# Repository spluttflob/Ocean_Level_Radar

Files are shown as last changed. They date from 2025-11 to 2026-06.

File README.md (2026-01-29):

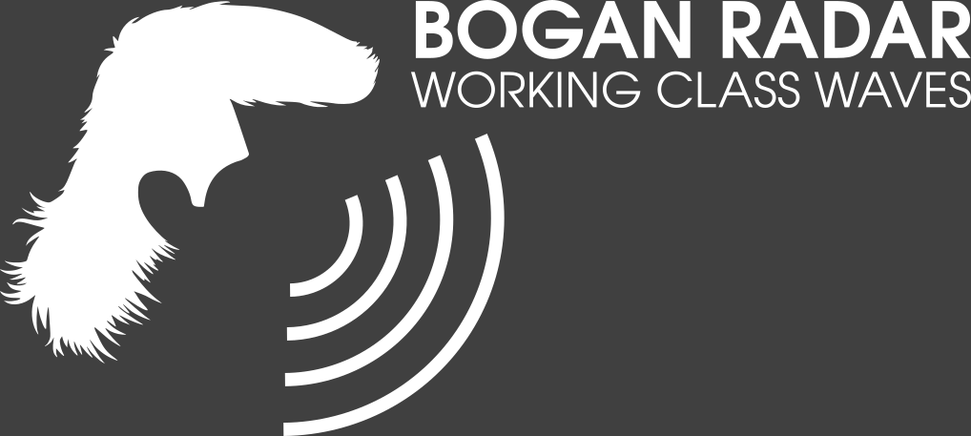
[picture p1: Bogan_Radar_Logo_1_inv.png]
Project logo


This project aims to create simple and inexpensive designs for measuring 
ocean level from piers, pilings, trees, or other relatively fixed
locations above the water.  THe measurements are to be taken quickly enough
that ocean waves and perhaps wind chop can be resolved. 
Ocean Science Hippies will use these measurements to better understand the 
effects of tides, waves, tsunamis, sea level rise, and other ocean phenomena 
on the coastal environment. 

## Hardware

The custom circuit board design currently used is in `hardware`. 

Mechanical part designs, including radar antennas and lenses, are currently 
being developed and will be added to this repository if and when we figure out
what on Earth we're doing. 

### Power

The current (2026 January) hardware versions may be powered by connecting the
ESP32 to a laptop through a USB cable, **or** by supplying the system with 
5 volts DC through the water resistant connector on the box. 

If a laptop cannot supply enough current through its USB port, the ESP32 may
reboot due to low supply voltage (it says `brownout detected`.)  Usually, 
rebooting a couple of times causes it to come to life; if that doesn't work, 
try another laptop and/or a powered USB hub. 

<span color="red">Only one source of power should be used at a time; **do not** 
connect the ESP32 Feather to a PC while DC power is being supplied through the 
waterproof connector.</span>

## Firmware

The software currently being developed uses a MicroPython program running on an
ESP32 as the overall controller, data logging, and network interface computer.
There is an STM32 microcontroller in the XM125 radar module which runs it own
software which is written in C. 

### ESP32 Firmware

There are two versions of the software which have been developed. The first
version is written in C++, and the second (and currently being worked on) 
version is in MicroPython.

#### C++

The C++ ESP32 firmware is in the `WaterSense_Radar_JJH` directory. 
After cloning this repository, open the `WaterSense_Radar_JJH` directory in a
VSCode/PlatformIO workspace and you should be able to compile and run the
ESP32 firmware. It requires custom firmware to be running on the STM32 in
the XM125 module.

#### MicroPython

For rapid development and testing, MicroPython firmware is provided in the
`MicroPython` folder.  MicroPython for the ESP32 can be downloaded from:  
<https://micropython.org/download/ESP32_GENERIC/>  
The latest release of the `ESP32_GENERIC` software is recommended for our
Feather circuit boards. 

With MicroPython installed on the ESP32, all the Python source files should 
be copied to the root directory of the ESP32's MicroPython filesystem, and 
`radar.cfg` should be copied to the root directory of the ESP32 file
system. Configuration of the system for use at specific sites may require 
editing of `main.py` and `task_mqtt.py`. The main Python file is edited to 
disable unneeded tasks; for example, the MQTT task should be turned off 
(just comment out the `asyncio.create_task()` line) at sites where WiFi 
access and AC power are not available. The radar's range, frequency of data 
collection, and similar configurations are set in `radar.cfg`. 

##### MicroPython File List

The following files need to be uploaded to the root directory of the ESP32's
MicroPython filesystem:

* `as_GPS.py` -- The asyncio GPS file from 
  <https://github.com/peterhinch/micropython-async/tree/master>
  or use the older, unmaintained copy here.
  
* `as_xm125_distance.py` -- From this repository.

* `main.py` -- From this repository.

* `mqtt_as.py` -- The asyncio MQTT client from
  <https://github.com/peterhinch/micropython-mqtt>
  or use the older, unmaintained copy here

* `pcf8523.py` -- Driver for the PCF8523 real-time clock on the Adalogger.
  Modified from others' work; use the copy here.
  
* `queue.py` -- From the standard MicroPython queues at 
  <https://github.com/peterhinch/micropython-async/tree/master>
  again, with an old local copy here for convenience.

* `task_gps.py` -- GPS task file from this repository.

* `task_mqtt.py` -- MQTT task (used if you have AC and WiFi) from this repository.

* `task_sd_card.py` -- SD card task from this repository.

* `radar.cfg` -- The configuration file for each site, put on the SD card.

#### Configuration with `radar.cfg`

The configuration file is a regular text file saved on the data logging SD card.
A typical configuration file might look as follows (for 2025-Dec version of the 
software; configurations are expected to change as the software is improved):
```txt
# Configuration file for Bogan Radar

Site Name:           My_Bench   # Name of site; should be one word (no spaces)
Beginning Distance:  2.0        # Beginning distance (m)
Ending Distance:     8.0        # Ending distance (m)
Sensitivity:         500        # Peak threshold sensitivity
Time Per Point:      5.0        # Time between data points (seconds)
Awake Time:          0.0        # Time taking data, sec., or 0.0 for always awake
Cycle Time:          0.0        # Total on-off cycle time, or 0.0 for always awake
```

_With changes to the value of `SD_DIR` in `task_sd_card.py`, the configuration
file could be saved in the ESP32's built-in flash; this would make reconfiguration 
a little harder but protect the configuration from SD card corruption due to power 
loss, somebody hot swapping the card (bad idea), etc._

If data is sent through MQTT, the MQTT topic is made by appending the site name
from the configuration file to `bogan_radar/`. 

### STM32 on XM125 Firmware

The STM32 microcontroller on the XM125 radar can be given a custom program to
optimize the radar module for our use. We have two setups available:

* When using the MicroPython firmware on the ESP32, the XM125's STM32 must be
  flashed with Acconeer's standard distance measurement application.
  The Acconeer software is available from:  
  <https://developer.acconeer.com/home/a121-docs-software/xm125-xe125/>  
  (You have to enroll with a developer account, but at least it's free to do 
  so.)

* When using the C++ firmware from directory `WaterSense_Radar_JJH` for the 
  ESP32, the source code for the STM32 microcontroller in the XM125 radar 
  module from subdirectory `xm125` must be compiled and flashed to the XM125.
  Compiling the XM125 STM32 code is a bit of a hassle, so we can use a binary 
  copy of the last working code.
  
* It's convenient to use an ST-Link2 programmer to flash the STM32 code to the 
  radar module. There is an ST-Link2 compatible 6-pin programming header near
  the screw terminal on the main circuit board, and there are two pushbuttons
  on the board to reset the STM32 and to put the STM32 in bootloader mode if 
  needed. 

## PC Software

### The _Acconeer Exploration Tool_

This handy application consists of a firmware package and a PC application.
Although it's designed to be run on an official Acconeer development board, the
Exploration Tool can also be run on our boards.

Instructions for setting up the STM32 firmware and Python PC software are at
<https://github.com/acconeer/acconeer-python-exploration>.  Follow Acconeer's 
instructions **with the following exceptions:**

* We usually use leftover ST-Link2 programmers (from old STM32 Nucleo&trade; boards) 
  instead of fussing with DFU programming.  The 6-pin ST-Link2 header next to 
  the power and battery connectors is connected directly to the 6-pin `SWD` (CN4) 
  connector on the ST-Link2, matching the ends marked with dots or triangles. 
  The STM32 Cube Programmer&trade; is a convenient way to flash the binary file
  for the firmware to the STM32. 

* To use our boards with the Exploration Tool, first remove the ESP32 Feather 
  board, any FeatherWing accsesory boards, and the GPS module from the main radar 
  circuit board. Leaving the GPS antenna in place, if present, is OK. 
  Then attach a connector (header pins or sockets) to the three-pin header pad
  marked `STM32 UART0` in the area where the GPS board sits.  Connect a USB to
  RS-232 serial adapter to STM32 UART0 pins, remembering the annoying RS-232 
  standard where RXD of one device must connect to TXD of the other. 
  If you're a civil, environmental, or mechanical engineer: Don't forget the 
  ground wire!  `:)`
  The Exploration Tool should now be able to connect to the XM125 as if the
  XM125 were on the official evaluation board. 

<!-- 
* Use ST-Link to load firmware
* Connect USB-Serial to ST's UART
* Set up Exploration Tool on PC
--> 

### Plotting MicroPython Data

If MicroPython is used, data will be saved in a Semicolon And Comma Separated
Variable (`.sacsv`) format. Some simple programs to plot data in this form are
being developed and can be found in the `CPython` directory. 

An older plotting program (look for lower numbers) uses data in a format 
without the date on each reading; this has caused some inconvenience, so newer
data is saved will a full datetime on every reading, and newer CPython scripts
with higher numbers in the file names use the newer format. 

### Plotting C++ Firmware Data

Some more fully Python developed programs to analyze data from the C++ firmware 
are in the `ESP32_to_Python_GUI` directory. 

It is our intention to merge the capabilities of the CPython programs from
the `CPython` and `ESP32_to_Python_GUI` directories to create especially 
convenient and flexible data analysis and plotting applications. 

## References

* A Masters thesis utilizing ultrasonic rather than radar sensors which gives
  some perspective to the project:  
  <https://digitalcommons.calpoly.edu/theses/2745/>

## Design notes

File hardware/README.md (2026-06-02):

# Bogan Radar Hardware Notes

**Version 1.4 (Still in alpha)**

This newer board is simpler and easier to assemble than V1.3.  All the SMD parts
are on one side of the board, so the SMDs can be soldered on first; a hot plate
works pretty well for this.  After the SMDs are in place, the through-hole parts 
can be attached to the other side.  The assembly of the board to the radar
antenna and installation in an enclosure are the same for both boards. 

**Version 1.3 (Obsolete; do not use)**

_**NOTE:** The 1.3 board version has not performed well enough in testing and is
considered obsolete. Newer boards are being prepared. The process of installing
the newer boards will be the same as that of installing older boards._

The current design uses the following bits:

* An Acconeer&trade; XM125 radar mounted to the bottom of a circuit board, with
  headers for many of the XM125 pins broken out to through holes on the board

* An Adalogger&trade; Featherwing for its SD card and battery backed up 
  real-time clock, mounted in a socket atop the board using stacking headers

* An ESP32 Feather board (EZSBC made boards preferred) mounted atop the 
  Adalogger
  
* A generic GPS receiver atop the circuit board

* A LiPo battery charging circuit built into the Feather board

The radar system is enclosed in a generic waterproof junction box. 
The board is mounted atop a horn-type millimeter-wave antenna that is attached
to the box with a waterproof seal.  The system is watertight so that it has a
chance to survive when deployed just above the ocean. 

_Note from testing: The enclosure shown has been tested in and survived 
several rainstorms, though a small amount of water was found in the bottom of
the box after about 6 weeks and several storms._

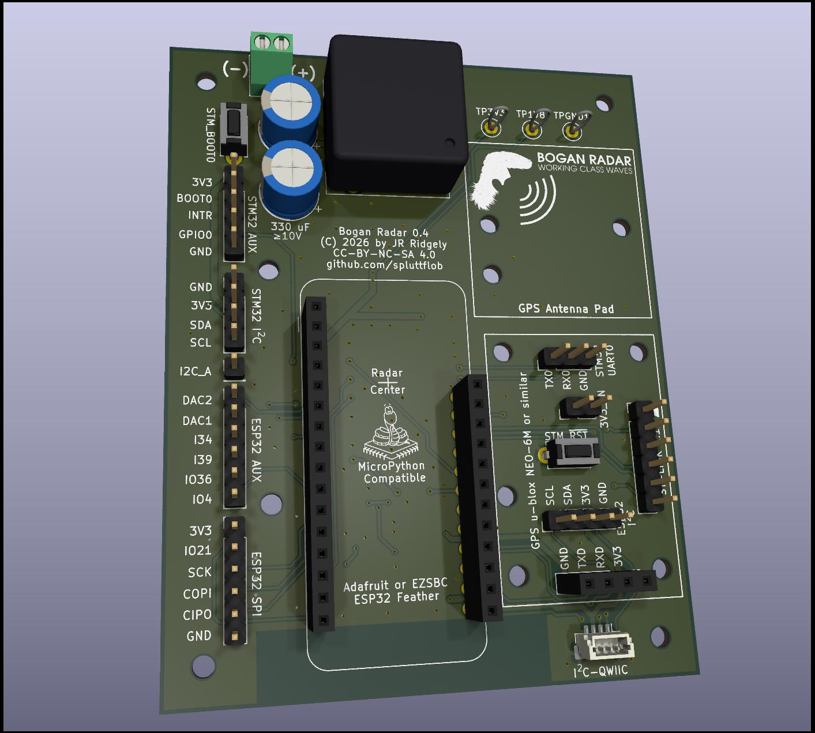
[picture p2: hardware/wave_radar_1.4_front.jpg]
Rendering of Board V1.4 Top Side


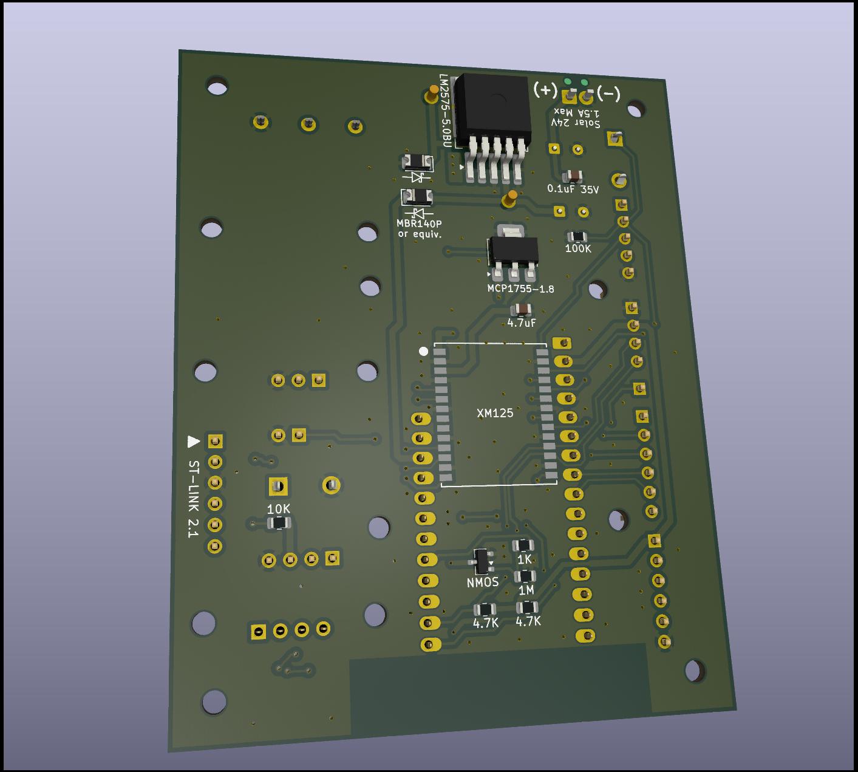
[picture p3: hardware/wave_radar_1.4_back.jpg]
Rendering of Board V1.4 Bottom Side


## Board V1.3 Hacks (legacy; use newer boards)

The design of the system has changed since a batch of the Version 1.3 boards
was manufactured, so there have been some hacks made involving jumper wires.
Please see [HACKS_1.3](HACKS_1.3.md) for details.

## RADAR Antenna

The horn antenna is a simple cylindrical design, manufactured mostly using a
lathe:

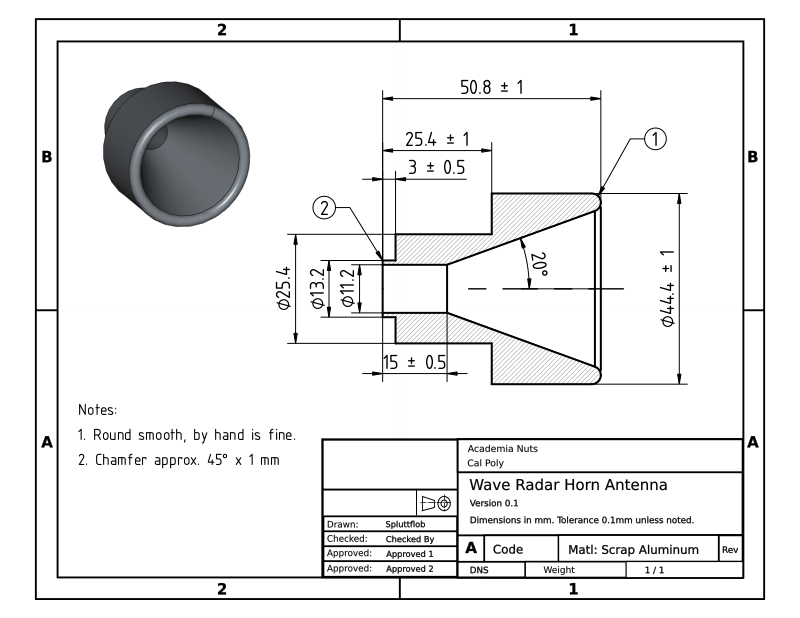
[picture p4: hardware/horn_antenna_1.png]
Drawing of Antenna


There are other antennas available such as plastic lenses. These may work well
also, and antenna testing and comparison are ongoing.

## Mounting in Enclosure

The branding of a typical enclosure is shown below.  This is not an endorsement
of this particular enclosure above others; it's just something we've tried:

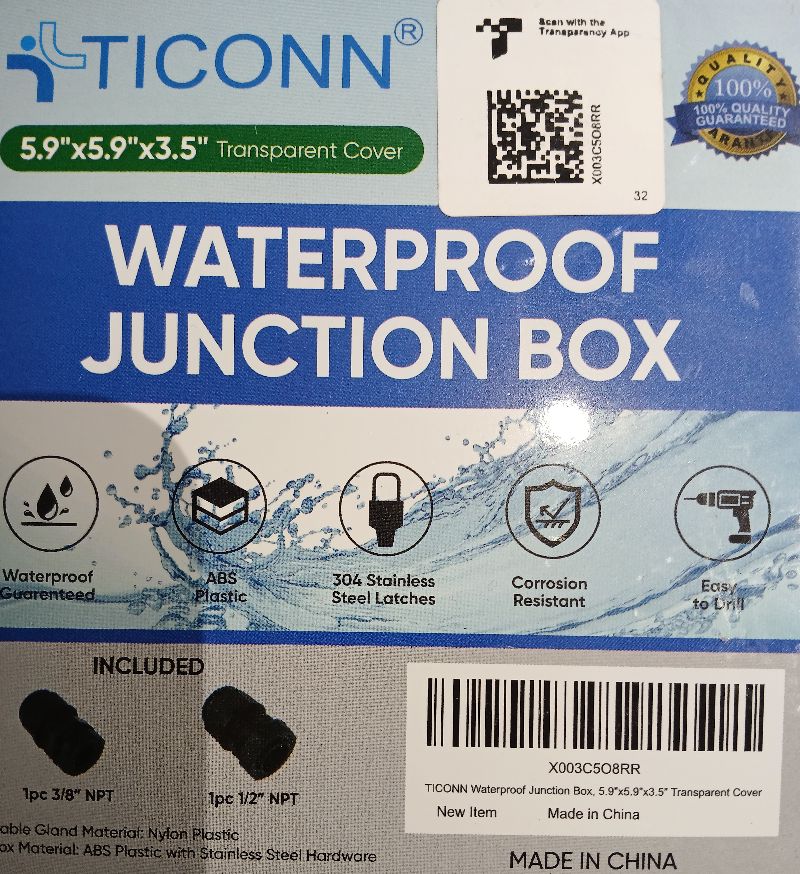
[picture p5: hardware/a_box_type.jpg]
Radar Box Brand


The antenna is mounted in the bottom of the box. A 1 inch hole is cut for the
antenna and the antenna is pushed in from the outside. We have had good results
using a step drill to make the hole.  Sealant is applied to
the flat mounting face of the antenna to prevent water ingress, and a couple of 
\#6-32 screws are tapped into the mounting face of the antenna to secure it to 
the box:

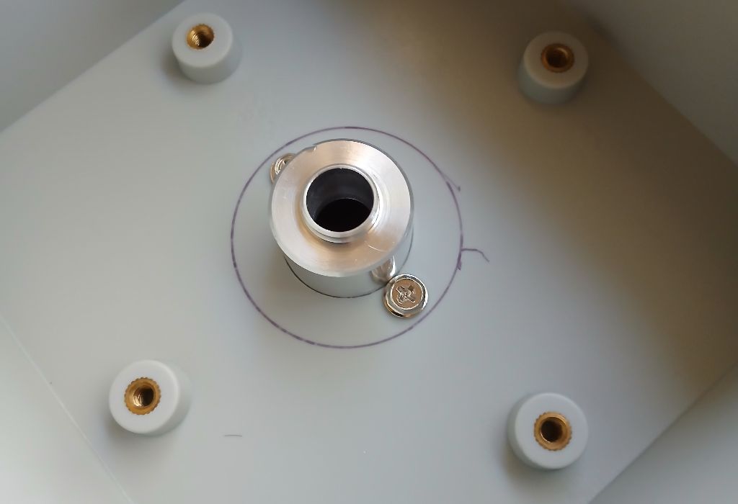
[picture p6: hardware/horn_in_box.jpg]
Box with Antenna Mounted


A 3D printed board mounting piece is attached to the upper side of the antenna 
to mount the circuit board. The end of the antenna must be flush with the slot
in the face of the board mount, as shown below using a ruler to verify that the
board mount is at the correct height. It's a little hard to see in the photo,
but the edge of the ruler is down in the slot, _not_ up on the faces of the
board mount that contact the board. This is critical because the XM125 sensor
will be in that slot when the board is mounted:

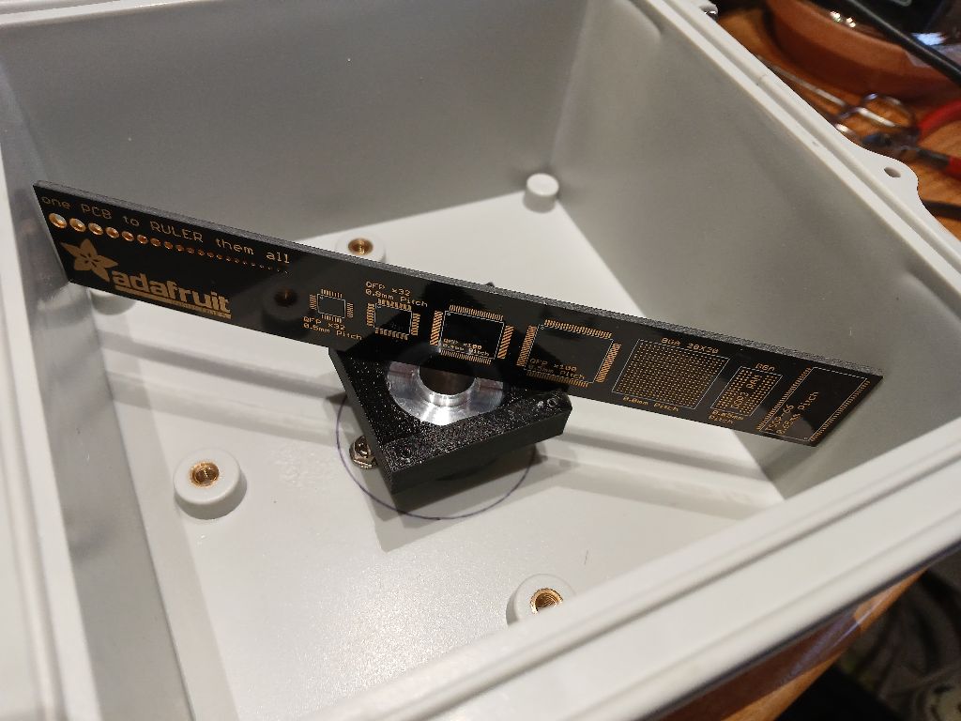
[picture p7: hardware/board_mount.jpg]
Attaching board mount at correct height


The board attaches to its mount with four annoyingly tiny screws. Ensure that
nobody sneezes to prevent losing the screws.  After the board is mounted, the
Featherwing, ESP32, and GPS can be inserted in their sockets and the electrical
power connection (see below) hooked up. 

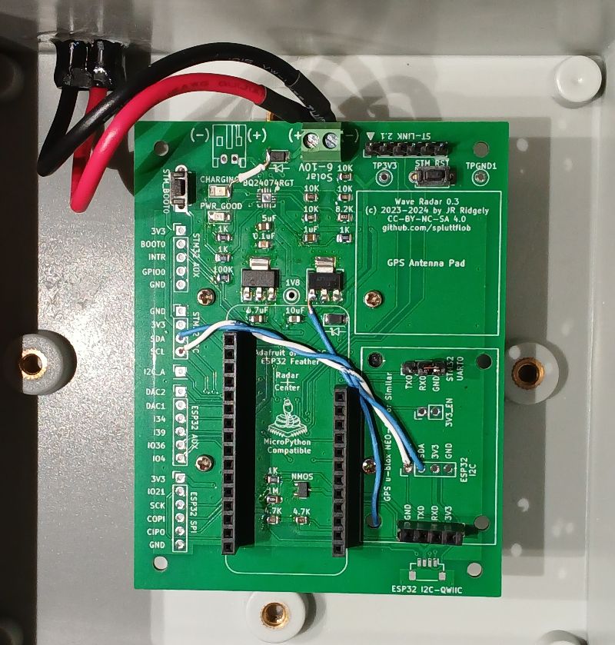
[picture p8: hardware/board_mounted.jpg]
Board attached to the board mount


The ESP32 Feather and Adalogger boards are stacked onto the Feather connectors
on the board in the usual way. Depending on the type of GPS module used, one
may need to mount the GPS antenna separately from the GPS module board.  If so,
the antenna can be mounted to the area marked `GPS Antenna Pad` on the board
with some double-sided foam tape. 
It is recommended to mount the GPS antenna so that the board mounting screw is
easily accessible with a screwdriver, as the need to remove the board for
updates or repairs is all but guaranteed in a research project. 

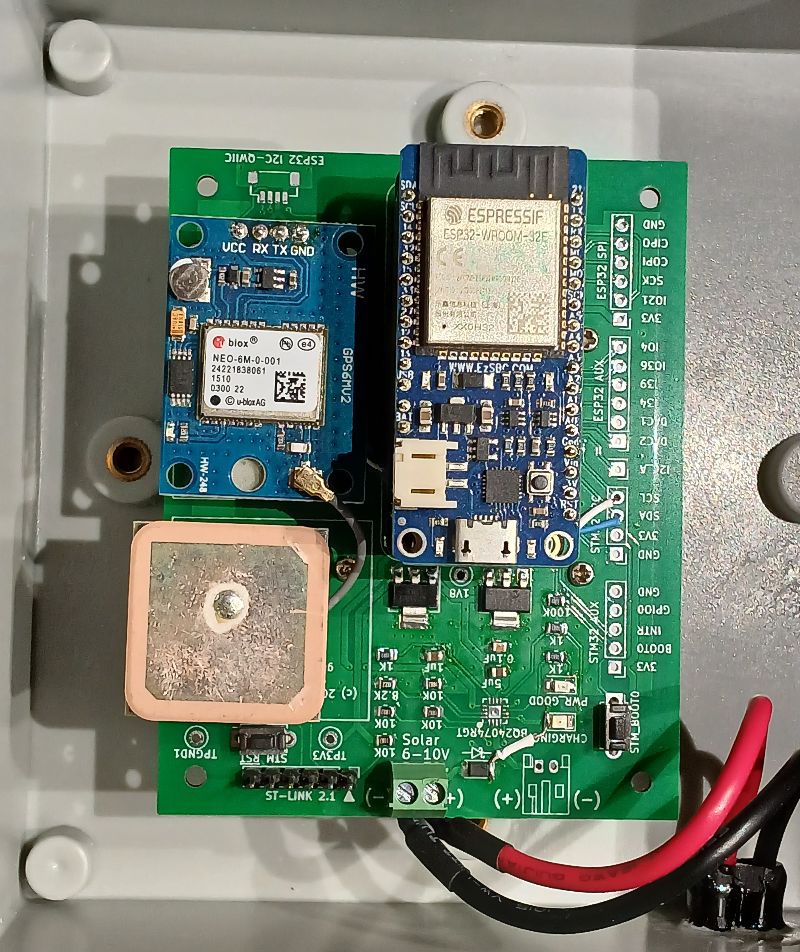
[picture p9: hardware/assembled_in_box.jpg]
Board with all parts attached


## Electrical Power Connection

For most uses, electricity must be supplied to the radar system from outside, 
either a solar panel or 5 volt wall plug adapter. _**Note:** The adapter should
be rated to produce 5.0 to 5.2 volts at around 1 amp. EZSBC boards are
designed to be supplied from 5 volt USB supplies and rated to handle up to 5.5
volts._  The power connection must be watertight.  In an experimental setup, we
have used an inexpensive waterproof automotive style connector glued into a hole
in the side of the box. 

## Radar Antenna Cover

This is an area of ongoing research. The radar may have an optimally tight beam
if a plastic phase corrector is attached across the bottom (wide) opening of
the horn antenna, but for initial testing we're trying polypropylene and
polyethylene disks made from various containers. The cover's ideal width which 
minimizes reflections of the 60GHz signal depends on the material used. 
The Interwebs seem to say that a 1.5mm (about 1/16") sheet of polypropylene 
would make a good cover. Disks of UHMW polyethylene (we think) cut from a
Tupperware&trade; bowl lid saved from a dumpster seem to work pretty well too.
More will be posted when we have conducted more experiments. 

Remember that the cover must be attached to the end of the horn with a 
watertight connection to protect the sensor from rain, waves, spray, and
errant organisms. A version of the aluminum horn antenna which has a threaded
end, combined with a threaded PVC ring that holds a cover firmly against the
end of the antenna, seems to work well.  We may use a bit of caulk or pipe
dope to ensure a good seal.

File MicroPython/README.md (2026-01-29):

# Bogan Radar MicroPython Setup

The MicroPython program used in the current (2026 January) version of Bogan 
Radar has the following features:

* Data taken from XM125 radar at intervals of 5 seconds, with moderate timing
  accuracy. A system timer is used to minimize clock drift; each reading may be
  some milliseconds late, but subsequent readings are then made sooner to keep
  the overall timing accuracy as good as possible using cotasks.

* Data is saved to an SD card. Every few minutes, the file is opened, a batch
  of data is written, and the file is closed immediately thereafter. Having the
  file open for only a short time reduces the likelihood of data corruption on
  the card due to power losses or program crashes. 

* The ESP32's Real Time Clock (RTC) is assisted by a PCF8523 RTC on the SD card
  (data logger) circuit board. With a backup battery, the PCF8523 keeps time
  with the main power off; the ESP32 RTC loses track of time when power is lost.
  A GPS receiver module is used to set both RTC clocks, as the RTC clocks are
  not highly accurate and may lose a few seconds each day. 

* Data may be transmitted to an MQTT broker for capture and storage on a 
  computer at a remote site. A Raspberry Pi in the developer's closet is used
  for testing, but any old computer which can run an MQTT client can do the job;
  a low-power device is recommended to avoid wasting lots of energy keeping a
  PC running 24/7. 

* A tiny web server allows anyone with network access to the ESP32 through LAN 
  or its access point to download data files from the SD card, _if_ the system
  has been set up with WiFi access or it is set up as an access point.  Since
  the WiFi module in the ESP32 takes a lot of power, this capability is likely
  to be used only where an AC mains connection is available to the radar unit.

* To keep the system going in case of unexpected crashes, a watchdog timer is
  used.  The hardware watchdog timer in the ESP32 is used as well as a set of
  asyncio events that require the radar, SD card, and MQTT tasks to be working
  to prevent system resets. 

## Saving RAM

The ESP32 WROOM module used has limited RAM, and MicroPython is fairly resource
heavy. The program as currently used will run out of RAM and crash if all the
files are regular Python source files. 

Therefore, we upload many of the utility programs as byte-compiled `*.mpy` 
files; this reduces RAM usage somewhat and enables the program to run reliably.
The program `mpy-cross`, which is part of the MicroPython source code
distribution, is used to byte-compile MicroPython source code into `.mpy` 
files. See:  
<https://pypi.org/project/mpy-cross/>

<https://github.com/micropython/micropython/tree/master/mpy-cross>

For a technical discussion of `.mpy` files (probably not needed), see:  
<https://docs.micropython.org/en/latest/reference/mpyfiles.html>

The main file and task files are usually kept as regular Python source files
because we're editing them often to change program behavior, fix bugs, _etc._

## What Files?

An image of the file listing from a working Bogan Radar ESP32 file system is
shown below.

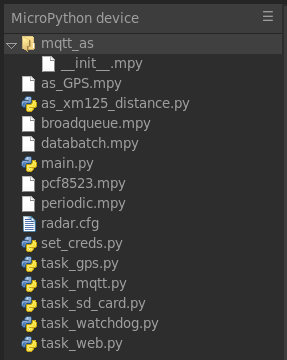
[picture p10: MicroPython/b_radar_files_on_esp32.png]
Device File List


It's a little weird that the asyncio MQTT server is in a file `__init__.py` in
the `mqtt_as` folder on the ESP32 filesystem. It's that way for reasons of
convenience due to how the `mqtt_as` system is distributed; it's easier to just
follow the distribution (with a small subset of its files to save space) than 
reorganize the package. 

## Configuration

We find the Thonny IDE at <http://thonny.org> convenient for editing files on 
the ESP32. 

* To change radar operating parameters such as site name, minimum and maximum 
distance to the water, and time between data points, edit `radar.cfg` on the
ESP32 filesystem. 

* To change the MQTT server and MQTT topic, edit `task_mqtt.py` where all the
  necessary information is in constants near the beginning of the file. 
  We've been using `test.mosquitto.org` for testing. 

* To set the LAN SSID and password:

  * Run the script `set_creds.py` on the ESP32. This script will define a
    function `setlan()` which allows the SSID and password to be stored in the
    ESP32's nonvolatile memory -- but it will _not_ run the function. 
    
  * You should then call the function, giving it the SSID and password of the
    access point you plan to use, for example:  
    `setlan("my_lan_name", "lamepassword")

If you're not using MQTT or the file server, turn off the tasks and make sure
the watchdog task won't be expecting the MQTT task to keep reporting to it:

In `main.py`:
```.py
    batch = databatch.DataBatch(POINTS_PER_DATA_BATCH,
                                maxsize=MAX_DATA_QUEUE_SIZE, drop_old=True)
    consumer_A = batch.register()
   # consumer_B = batch.register()

    tasks = []
    tasks.append(asyncio.create_task(task_sd_card.task_SD_Card(consumer_A)))
   # tasks.append(asyncio.create_task(task_mqtt.mqtt_task(consumer_B)))
    tasks.append(asyncio.create_task(task_gps.gps_task(i2c, batch)))
    tasks.append(asyncio.create_task(task_radar(batch)))
    tasks.append(asyncio.create_task(task_watchdog.task_watchdog()))
   # asyncio.create_task(task_web.file_server_task())
```

In `task_watchdog.py`:
```.py
    await asyncio.gather( # mqtt_event.wait(),
                        sd_card_event.wait(),
                        radar_event.wait())
```

At this time, the file server task relies on the MQTT task to keep up a network
connection, so those two tasks must be activated or deactivated together. 
A future project should be to make an independent task which keeps the network
going for only the file server task. In addition, the web server could be 
kept off to save energy unless it is activated by some mechanism such as a
physical switch.

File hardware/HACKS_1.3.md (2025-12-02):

# Bogan Radar Board V1.3 Hacks

## I&sup2;C Connections

The method of communication between the ESP32 system control and networking 
microcontroller and the STM32 microcontroller on the XM125 radar board has been
changed from RS-232 to I&sup2;C.  Therefore, jumper wires must be connected 
between the ESP32's I&sup2;C terminals and those of the STM32. The twisted blue 
and white wires boing mostly left to right in the photo below connect the 
I&sup2;C signals. 

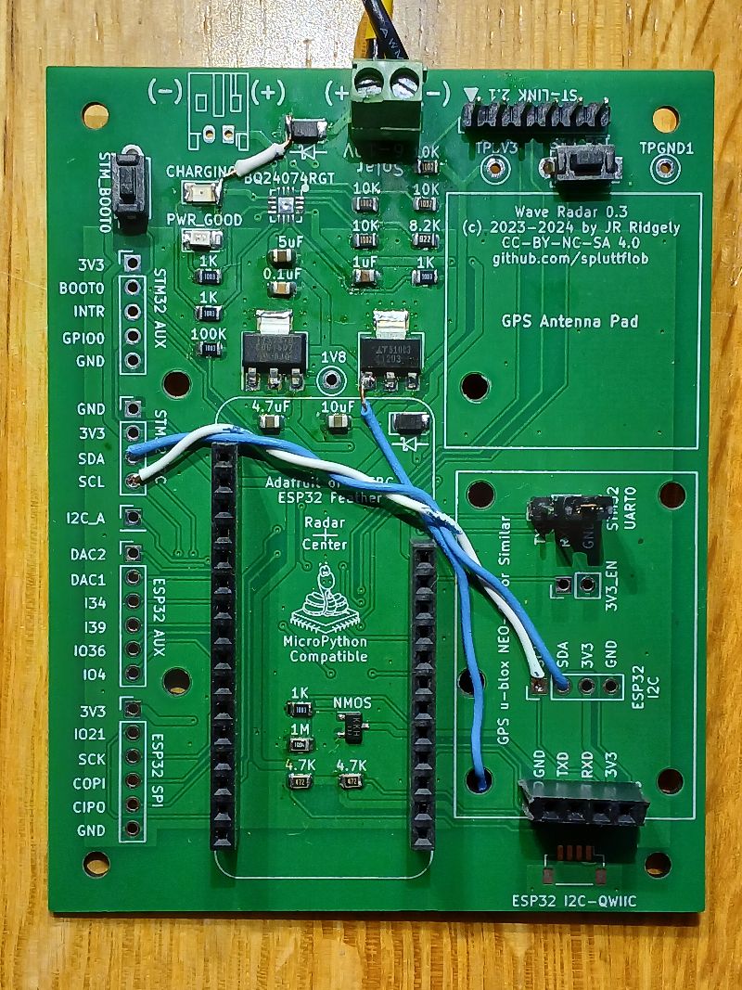
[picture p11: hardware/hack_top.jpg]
Main board with jumper wires all over


If the main board has been assembled correctly, the two 4.7K I&sup2;C pullup
resistors are already present. 

## AC _vs._ Solar and Battery Power

When deployed near a usable source of AC power, the radar system may be supplied
from a 5V DC adapter connected through the solar panel input. This connection is
made using the screw terminal at the top of the image above. _**Note:** 
Significantly higher voltages such as 12V should **not** be used, as the
regulators on the ESP32 Feather board are designed for 5V USB input and not
safe with higher voltages._ 

When using AC power, we can leave the BQ24074RGT charge controller off the 
board, bypassing it with a short wire such as the short white wire seen from
the right side of the CHARGING LED to the left side of the Schottky diode near
the screw terminals.  This supplies power to the 1.8V and 3.3V regulators on
the main board. 

In addition, power must be supplied directly from the input to the regulators
to the ESP32 Feather's USB power input.  The blue wire attached to the input
pin of the 3.3V regulator and extending downwards through an unused mounting
hole on the board does this.  This wire is connected to the ESP32 USB pin on 
the bottom of the board as seen in the photo below. 

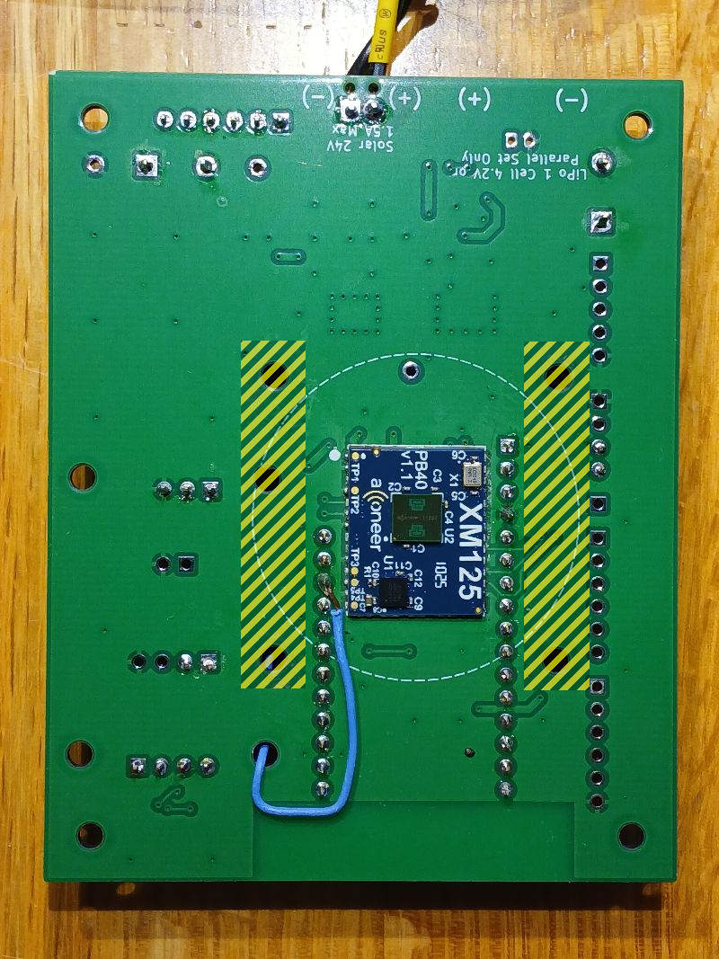
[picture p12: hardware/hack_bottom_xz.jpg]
Back of main board with a jumper


_**Note:** The jumper wire should not pass through the holes which are closer
to the XM125 because doing so will interfere with the mounting fixture and 
screws that are used to attach the board to the antenna. The board must be
mounted correctly to the antenna for a strong signal to be received.  Also
note that the wire is on the right side of the Feather mounting pins because
the board mounting fixture must be up against the board on the left side; the
approximate area where the board contacts the mounting fixture is crosshatched
in the image above._

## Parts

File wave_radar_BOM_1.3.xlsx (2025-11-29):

BOM For Wave Radar Version 1 -- Last Updated Nov. 2025
Parts on PCB (Board version 0.2) |  |  |  |  | Some quantities are greater than fit on boards to provide spares and/or take advantage of quantity pricing.
 | Id | Designator | Footprint | Brd.Qty. | Designation | Qty. For 5 Units | Cost / 5 Boards | Supplier and ref
 | 4 | J5 | JST_SH_BM04B-SRSS-TB_1x04-1MP_P1.00mm_Vertical | 1 | I2C-QWIIC | 1 pack | $3.95 | https://www.adafruit.com/product/4208 | Not needed for current system
 | 5 | R4 | R_0805_2012Metric | 1 | 8.2K | 10 | $0.07 | https://www.mouser.com/ProductDetail/YAGEO/RC0805JR-078K2L?qs=KyGMWp10UkvZ9xktQXin5g%3D%3D
 | 6 | J9 | JST_PH_S2B-PH-K_1x02_P2.00mm_Horizontal | 1 | LiPo | 5 | $0.90 | https://www.digikey.com/en/products/detail/jst-sales-america-inc/S2B-PH-K-S/926626
 |  |  | Mouser listing for S2B-PH-K connector above (I think!) | 1 |  | 10 | $2.27 | https://www.mouser.com/ProductDetail/JST-Commercial/S2B-PH-K-S-GWPP
 |  |  | Pushbutton switches...out of stock 2025-Nov-10 |  |  | 10 |  | https://www.mouser.com/ProductDetail/Apem/MJTP1243?qs=Uv2m1HzDAyqvmQR%252Bfj6VKQ%3D%3D
 | 10 | J10 | PinSocket_1x04_P2.54mm_Vertical | 1 | GPS | 5 | $3.97 | https://www.mouser.com/ProductDetail/Harwin/M20-7820442?qs=vF78I%252BjhbY9ZgDLCXkGx4w%3D%3D
 | 11 | R10,R9,R3,R8 | R_0805_2012Metric | 4 | 1K | 25 | $1.07 | https://www.mouser.com/ProductDetail/Bourns/CRT0805-FZ-1001ELF?qs=zVPOhnWuw8XKnszaWxnxVA%3D%3D
 | 12 | D3 | LED_1206_3216Metric (yellow) | 1 | CHARGING | 10 | $2.43 | https://www.mouser.com/ProductDetail/Kingbright/APD3224SYCK-F01?qs=VdjlWU%2FzoOF7uyPL3qtctA%3D%3D
 | 30 | D2 | LED_1206_3216Metric (green or blue) | 1 | PWR_GOOD | 10 | $2.49 | https://www.mouser.com/ProductDetail/Kingbright/APD3224SGC-F01?qs=VdjlWU%2FzoOFlLUgo8Vdl7g%3D%3D
 | 13 | Q1 | SOT-23 | 1 | NMOS | 10 | $2.40 | https://www.mouser.com/ProductDetail/onsemi-Fairchild/FDV303N?qs=FOlmdCx%252BAA1IyXspysHTkA%3D%3D
 | 16 | R2,R1 | R_0805_2012Metric | 2 | 4.7K | 15 | $0.24 | https://www.mouser.com/ProductDetail/YAGEO/RC0805JR-074K7P?qs=oypCK0zG327lNRTQ3ak4YQ%3D%3D
 | 19 | C2 | C_0805_2012Metric | 1 | 10uF | 10 | $1.65 | https://www.mouser.com/ProductDetail/Murata-Electronics/GRM21BC81D106KE51K?qs=QzBtWTOodeX3BXZzorRwZw%3D%3D
 | 20 | R13 | R_0805_2012Metric | 1 | 100K | 10 | $0.33 | https://www.mouser.com/ProductDetail/Vishay-Dale/CRCW0805100KJNTA?qs=rGO4O3Mig4idWRslNBLx9A%3D%3D
 |  |  | Headers for ESP32 Feather board below | 1 |  | 5 | $7.50 | https://www.adafruit.com/product/2940
 |  |  |  |  |  |  | same as above | https://www.mouser.com/ProductDetail/Adafruit/2940
 | 23 | C4,C1 | C_0805_2012Metric | 1 | 1uF | 10 | $1.59 | https://www.mouser.com/ProductDetail/KEMET/C0805C105J4RAC7210?qs=7zB%252BIQS%2FKOJG%252BUtduyFhHw%3D%3D
 | 26 | D1,D4 | D_1206_3216Metric | 2 | D_Schottky | 10 | $2.50 | https://www.mouser.com/ProductDetail/KYOCERA-AVX/SD1206T040S1R0?qs=jCA%252BPfw4LHbR43TXEWb5mg%3D%3D
 | 28 | U4 | VQFN-16-1EP_3x3mm_P0.5mm_EP1.6x1.6mm | 1 | BQ24074RGT | 7 | $13.16 | https://www.mouser.com/ProductDetail/Texas-Instruments/BQ24074RGTRG4?qs=drm0CCHqiV5LjyrmJlyFDQ%3D%3D
 |  |  |  |  | Capacitor, 4.7uF | 10 | $1.81 | https://www.mouser.com/ProductDetail/KEMET/C0805C475K3PACTU?qs=K%2Fj%2Fqf%252B0fqKgIgOb3tBMNw%3D%3D
 | 31 | C5 | C_0805_2012Metric | 1 | 0.1uF | 10 | $0.52 | https://www.mouser.com/ProductDetail/YAGEO/CC0805JRX7R8BB104?qs=AgBp2OyFlx%252BZU4KTc42Krw%3D%3D
 | 32 | J8 | TerminalBlock_Phoenix_MPT-0,5-2-2.54_1x02_P2.54mm_Horizontal | 1 | Solar | 5 | $4.75 | https://www.adafruit.com/product/2138
 |  |  |  |  |  |  | same as above | https://www.mouser.com/ProductDetail/Adafruit/2138
 | 33 | R11 | R_0805_2012Metric | 1 | 1M | 10 | $0.19 | https://www.mouser.com/ProductDetail/Vishay-Dale/CRCW08051M00JNEAC?qs=E3Y5ESvWgWMKh2Fxw4eXlg%3D%3D
 | 34 | U1 | LT1129 | 1 | LT1129-3.3_SOT223 | 5 | $48.10 | https://www.mouser.com/ProductDetail/Analog-Devices/LT1129CST-3.3PBF
 | 36 | U2 | MCP1754S | 1 | MCP1754S-1802xMB | 5 | $3.65 | https://www.mouser.com/ProductDetail/Microchip-Technology/MCP1754ST-1802E-MB
 | 37 | U3 | XM125_ACC radar unit | 1 | XM125 | 3 | $55.80 | https://www.mouser.com/ProductDetail/Acconeer/XM125?qs=sGAEpiMZZMu3sxpa5v1qruw6EePLcCCpnJBrB4hYxzU%3D
 |  |  |  |  |  | Total for 5 Boards | $161.35
GPS Modules, SD Card Adapter, ...
 |  |  | GPS module with uBlox receiver and fancy antenna | 1 |  | 5 | $44.95 | https://www.amazon.com/HiLetgo-GY-NEO6MV2-Controller-Ceramic-Antenna/dp/B01D1D0F5M/ref=sr_1_11
 |  |  | Adalogger: SD card adapter for ESP32 microcontroller | 1 |  | 5 | $44.75 | https://www.mouser.com/ProductDetail/Adafruit/2922
 |  |  | Lithium cell for Adalogger | 1 |  | 5 | $8.99 | https://www.amazon.com/Panasonic-Lithium-Batteries-Size-CR1220/dp/B005FX02MI/
 |  |  | Stacking header set for Adalogger | 1 |  | 5 | $6.25 | https://www.mouser.com/ProductDetail/Adafruit/2830
Lens for Board High Above Water |  |  |  | Note: We might not need lenses unless more than 3-5m up, pending tests
 | 1 | Acconeer Lens Kit: Not sure this is what we need; we should consider making our own lenses |  |  |  | 0 | $0.00 | https://www.mouser.com/ProductDetail/Acconeer/LH120?qs=tlsG%2FOw5FFghGQJlh%2F9x2A%3D%3D
 | 2 | 3D printed lens holder if using lens kit above is on listed GitHub site |  |  |  |  |  | https://github.com/spluttflob/Wave-Radar/tree/main/mech
 |  | If making our own lenses, maybe print 'em with integrated holders
LiPo Cell
 |  |  | LiPo battery, these are the ones we currently use on the project |  |  | 3 | $89.85 | https://www.adafruit.com/product/5035
 |  |  |  |  |  |  |  | https://www.mouser.com/ProductDetail/Adafruit/5035?qs=pBJMDPsKWf13hGA%252B7pfQ3w%3D%3D
ESP32 Circuit Boards and Add-ons
 | 21 | A1 | Adafruit_Feather(Headers attached) | 1 | Feather_ESP32 | 0 | $0.00 | https://www.adafruit.com/product/3405
 |  | Note: Many Adafruit products are available from Mouser and/or Digikey.

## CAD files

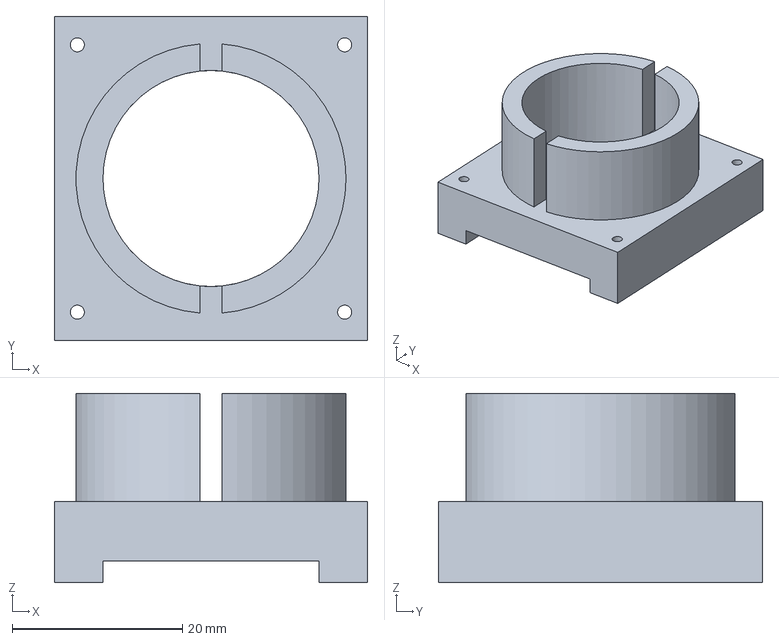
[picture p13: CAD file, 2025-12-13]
hardware/antenna_holder.FCStd
36.8 x 38.1 x 22.2 mm

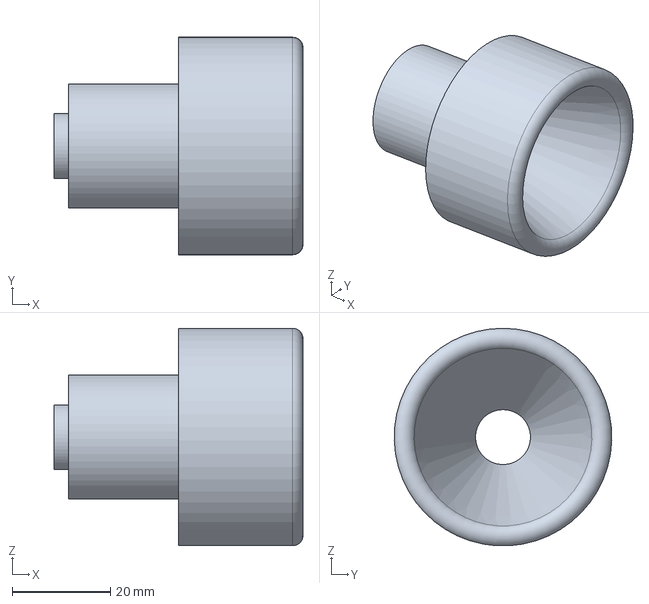
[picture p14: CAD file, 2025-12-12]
hardware/horn_antenna_1.FCStd
50.8 x 44.4 x 44.4 mm

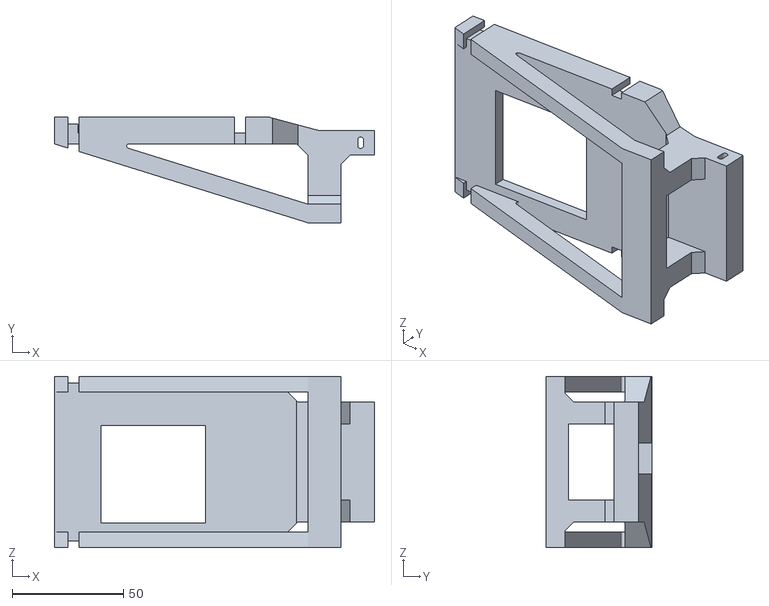
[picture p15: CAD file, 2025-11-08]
hardware/QTY1_radar_mount_A.STL
144.0 x 47.5 x 77.0

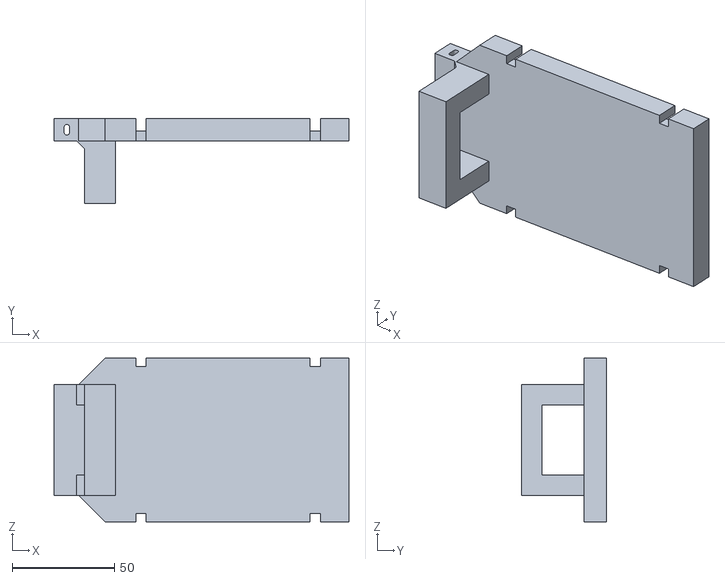
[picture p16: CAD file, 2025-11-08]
hardware/QTY1_radar_mount_B.STL
144.0 x 41.5 x 80.0

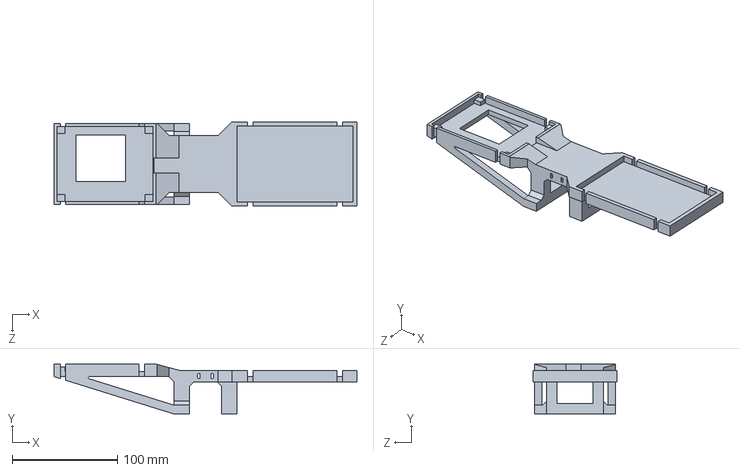
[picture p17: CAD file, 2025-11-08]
hardware/stick_mount.SLDPRT
288.0 x 47.5 x 80.0 mm

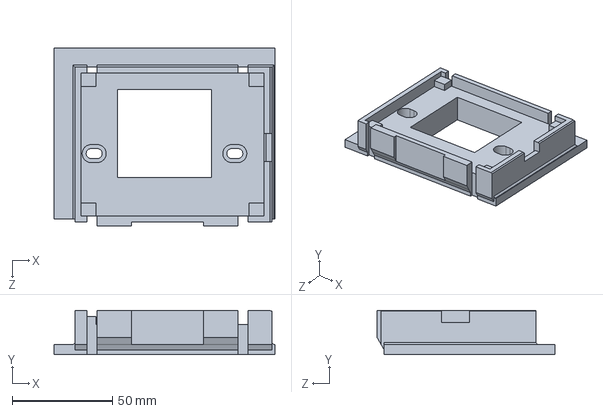
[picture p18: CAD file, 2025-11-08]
hardware/box_mount.SLDPRT
110.0 x 22.0 x 88.5 mm

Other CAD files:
hardware/antenna_holder.stl

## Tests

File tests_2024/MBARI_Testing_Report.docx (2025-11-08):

Monterey Bay Aquarium Research Institute Testing Report

Jakob Frabosilio, Student Assistant
Cal Poly SLO Mechanical Engineering Department
12/2/2024

Summary

The radar unit was tested at the Morro Bay Yacht Club on 10/27. The results show that small waves (1-2Hz, 2-10cm peak-to-peak) can be accurately measured on still water given proper configuration of the radar; Figure 0 shows a highlight of the test results. Additionally, the water level height decreasing with the tide was clear over the course of data collection; tide data can be accurately measured with the radar unit in its present form.

The testing was critical for finding optimal settings for the radar unit configuration and for identifying bugs in the firmware implementation. Future testing is planned at the Monterey Bay Aquarium Research Institute (MBARI) in Moss Landing from Nov. 15-17th (King Tides event) to test the long-term data collection of the radar unit.

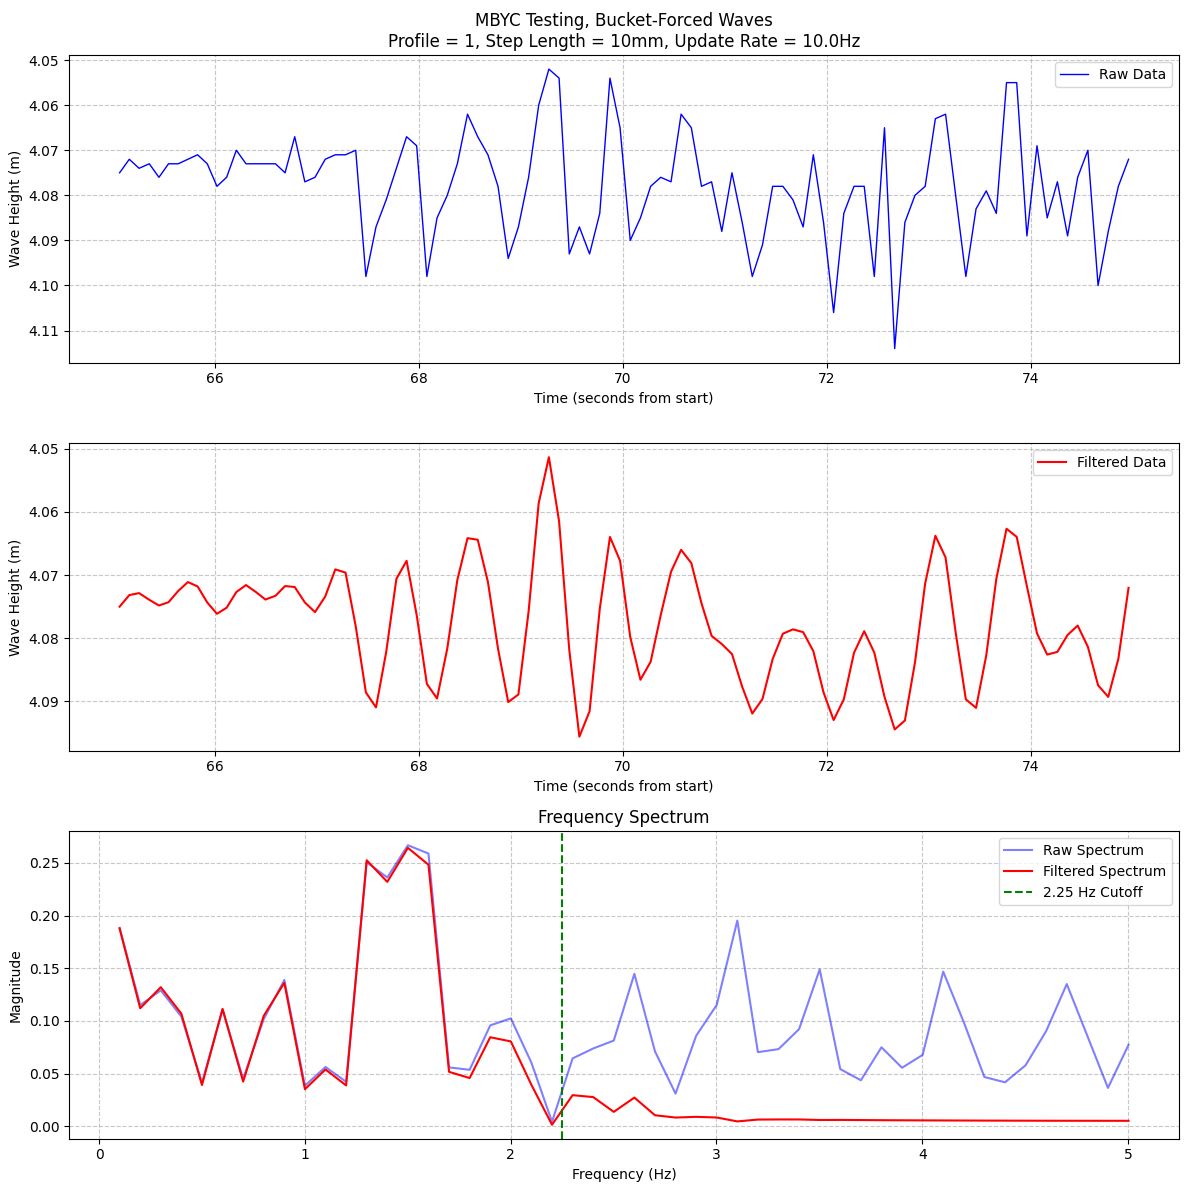
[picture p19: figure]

Figure 0. Best results from MBYC testing; profile = 1, update rate = 10Hz

Introduction

On Sunday, October 27th, the low-cost water level gauge (“radar unit”) was tested at the Morro Bay Yacht Club with Dr. John Ridgely and Dr. Serena Lee. The purpose of the testing was to determine if small, rapid displacements in the water could be detected by the radar unit from a considerable distance away.

The radar unit was attached to an elevated dock approximately 4m above the surface of the water, sticking out approximately 50cm from the edge of the dock. The unit was powered using a 25W solar panel and a 5V solar power battery bank to ensure no power loss. The final implementation will use a solar panel with considerably less wattage – this panel was used for convenience. See Figure 1 for an image of the radar unit in its testing position.

Due to the still nature of the water below the dock (inside of a harbor on a windless day, protected from external waves by a floating dock), a bucket was attached to the end of a rope and was used to create controlled waves. The bucket was partially filled with water and was hoisted up and down repeatedly at a regular interval to create waves of a relatively known amplitude and frequency (roughly 2-10cm peak-to-peak amplitude and 1-2Hz frequency). See Figure 2 for an image of the bucket in the test environment. Note that some of the waves created by the bucket can be seen in the background of the image.

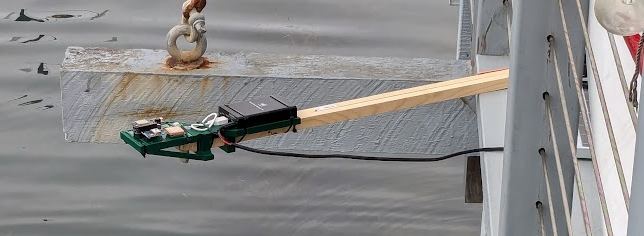
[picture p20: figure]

Figure 1. Radar unit suspended over the water surface, attached to the deck of the Morro Bay Yacht Club

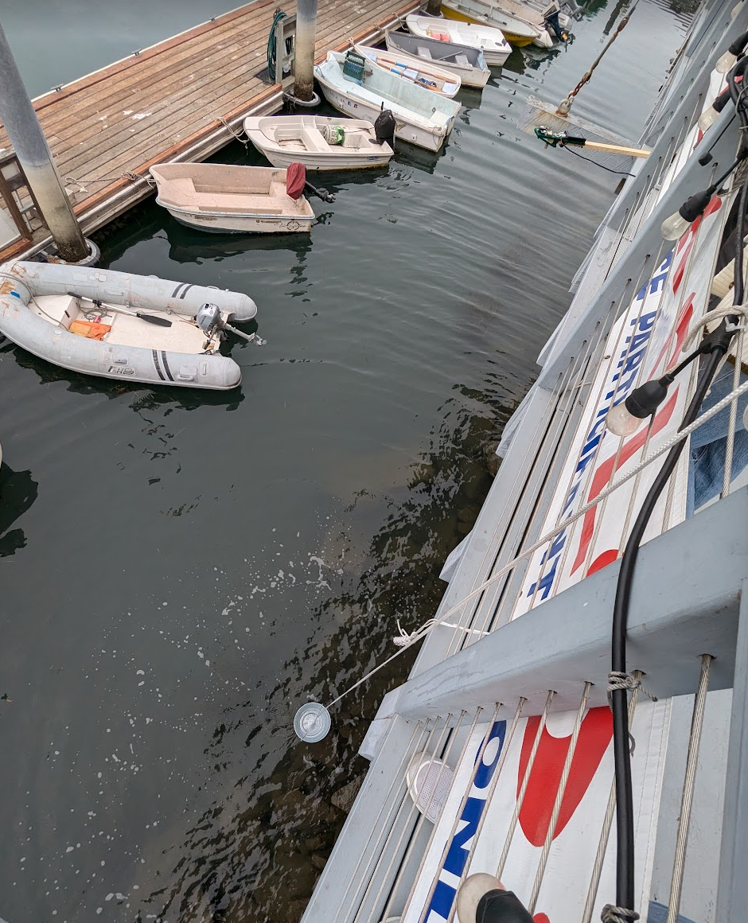
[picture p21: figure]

Figure 2. Bucket and rope in foreground, used for controlling waves, with radar unit and waves in the background

Test Plan and Procedure

After an initial set-up and calibration period to ensure good measurements, a series of tests were performed to determine the optimal radar configuration settings. Three different settings were varied throughout the testing:

- Maximum Profile (1, 3, 5)
  - Determines the duration and shape of the radar burst. A higher profile setting (5) increases the signal-to-noise ratio but decreases the maximum update rate.
  - Additionally, higher profile settings can make it difficult to distinguish between multiple objects in a scene, as seen in Figure 3.
- Maximum Step Length (5mm, 10mm, 15mm)
  - Determines the maximum distance between radar measurements. A lower maximum step length results in more measurements taken for a given measurement range, increasing the power consumption and decreasing the update rate, but returning more accurate measurements for small displacements.
  - The radar works by sending out pulses and measuring the return in discrete intervals. If the start range of the radar is set to 1m and the end range is set to 2m, the step length determines how that range is subdivided. For a max step length of 100mm, the radar would test the return strength at 1m, 1.1m, 1.2m, etc. until it hits 2m.
  - The radar unit uses phase data to interpolate between these measurements. If an object is located at 1.05m, the radar unit can still detect it using a step length of 100mm, despite the object not appearing directly at a measured distance.
- Update Rate (5Hz, 10Hz)
  - Determines how often measurements are taken. Limited by other configuration settings (profile, step length, measurement range), and increases power draw as it rises.
  - Higher update rates are required to measure waves with higher frequencies. To measure waves with a frequency of 2Hz, a minimum 4Hz update rate is required. Generally, higher frequencies produce cleaner data in this application.

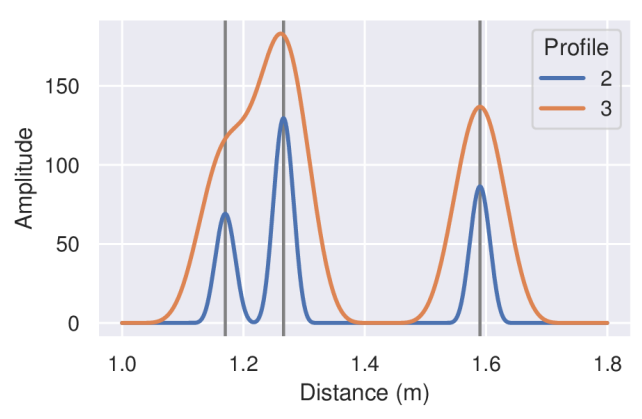
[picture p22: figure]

Figure 3. Mock data for different maximum profile settings, three objects in measurement range; Profile=2 captures all three objects, while Profile=3 incorrectly combines the first and second object

Note that there are other configuration settings beyond these three for the radar unit; these three are simply the most important to tune for this application, especially given the power consumption requirements.

A total of 12 tests were conducted using combinations of the above settings. The table below summarizes the configuration for each test, as well as its start time.

Test Number | Start Time (PDT) | Max Profile | Max Step Length | Update Rate
1 | 12:57pm | 3 | 5mm | 5Hz
2 | 1:00pm | 5 | 5mm | 5Hz
3 | 1:04pm | 1 | 5mm | 5Hz
4 | 1:09pm | 3 | 10mm | 5Hz
5 | 1:12pm | 5 | 10mm | 5Hz
6 | 1:16pm | 1 | 10mm | 5Hz
7 | 1:22pm | 3 | 15mm | 5Hz
8 | 1:27pm | 5 | 15mm | 5Hz
9 | 1:31pm | 1 | 15mm | 5Hz
10 | 1:38pm | 5 | 10mm | 10Hz
11 | 1:45pm | 1 | 10mm | 10Hz
12 | 1:49pm | 3 | 10mm | 10Hz

For each test, the following procedure was carried out:

- Place the bucket in the water approximately 3m from the center of the radar unit, measured horizontally
- Wait until the water below the sensor is still before beginning the test
- After starting data collection, wait approximately 10-20 seconds to collect still water readings (no waves, minimal noise; flat surface)
- Raise and lower the bucket approximately 20cm (peak-to-peak) using the rope at a rate of 1-2Hz for approximately 20 seconds
- Wait for the water to settle, approximately 20 seconds
- Raise and lower the bucket as before, but with a greater amplitude (and more splashing / noise)
- Continue collecting data for 20 seconds after the second round of bucket hoisting

Figure 4 shows the results of an average test as measured by the radar unit. Note that the y-axis is flipped; the radar unit currently measures the distance from the unit’s lens to the surface of the water, so a wave with positive displacement (or a rising tide) means that the measured distance decreases. In the future, the elevation data of the radar unit will be incorporated to convert the relative-distance measurements into absolute height measurements (relative to average sea level).

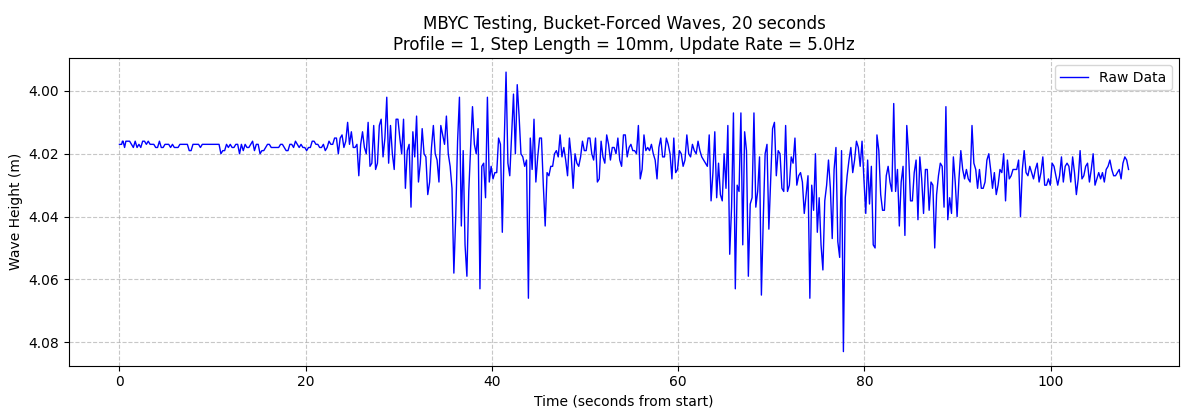
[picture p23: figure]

Figure 4. Test 6 full results from radar unit

Results and Analysis

All tests produced similar results for the first portion of the procedure (measuring only the still water) – the average noise in these readings is around 1cm peak-to-peak for all tests. Figure 5 shows the first five seconds of data collection for three different tests. The profile, step length, and update rate have little-to-no effect on the noise floor for still water.

To determine which settings are most “optimal” or “accurate” is difficult, given that the true wave amplitude and frequency were only estimated visually. However, a few key items are known that will aid in analysis:

- The true wave frequency (waves created by the bucket hoisting up and down) is between 1-2Hz; if the primary frequencies in the radar data are between these values, then the wave is likely being recorded properly.
- The true wave amplitude is roughly between 2-10cm peak-to-peak; if the amplitude of the measured waves is significantly higher than this range, then there is likely significant noise in the measurements.

The maximum profile appears to have a large impact on the quality of the measurements. Figure 6 shows a comparison between profile settings of 1, 3, and 5; as the profile increases, the noise during these wave measurements increases dramatically. Note that the profile=5 test measured wave amplitudes much higher than 10cm peak-to-peak.

Additionally, a frequency analysis of these tests shows that the true wave frequency (between 1-2Hz) is much more prevalent in the profile=1 test than the profile=5 test; see Figures 7 and 8 respectively for these tests. Given these results (and the fact that higher profiles increase the power consumption and lower the maximum update rate significantly), it is recommended that the profile be set as low as possible.

The step length did not appear to have a large impact on the accuracy of the results. Figure 9 shows a comparison of three different step length settings with profile = 1. The wave amplitudes and frequency components are comparable for the three tests. Future testing, with a way to verify the true height of the waves, is required to determine optimal settings for the step length. At present, it is recommended that the step length be set as high as possible to decrease power consumption and increase the maximum update rate.

The update rate has a large impact on the quality of the results, given the wave frequency of 1-2Hz. An update rate of 5Hz was slightly low to cleanly capture the waves created by the bucket; increasing the rate to 10Hz yielded much better results. Compare Figures 10 and 11; the higher update rate (combined with a low-pass filter to remove high-frequency noise components) produced very clear measurements of the bucket-forced waves. It is recommended to set the update rate as high as possible to accurately capture the profile of high-frequency waves. 10Hz appears to be a good compromise between power consumption and accuracy.

All testing was conducted over the course of an hour; on the day of testing, the high tide was around 9am and low tide was around 2pm. The estimated water level drop across the testing period, using tide data from tide-forecast.com, was approximately 0.12m. Figure 12 shows all of the testing data concatenated, with the tide drop clearly present.

The lack of a smooth line is due to the changing configuration of the radar for each test; changing the measurement profile affects the “average” readings of the water level. For the highest profile (Tests 2, 5, 8, and 10), the average water level measured was slightly higher than adjacent tests. With higher profiles, more energy is sent in the radar burst; it is assumed that these higher energy levels reflect off the surface of the water earlier (with lower profile bursts penetrating the water slightly more). The tide data can be easily measured using any settings of the radar unit, but the profile slightly affects the average water height reading. Further testing and improved implementation are required to accurately characterize this behavior.

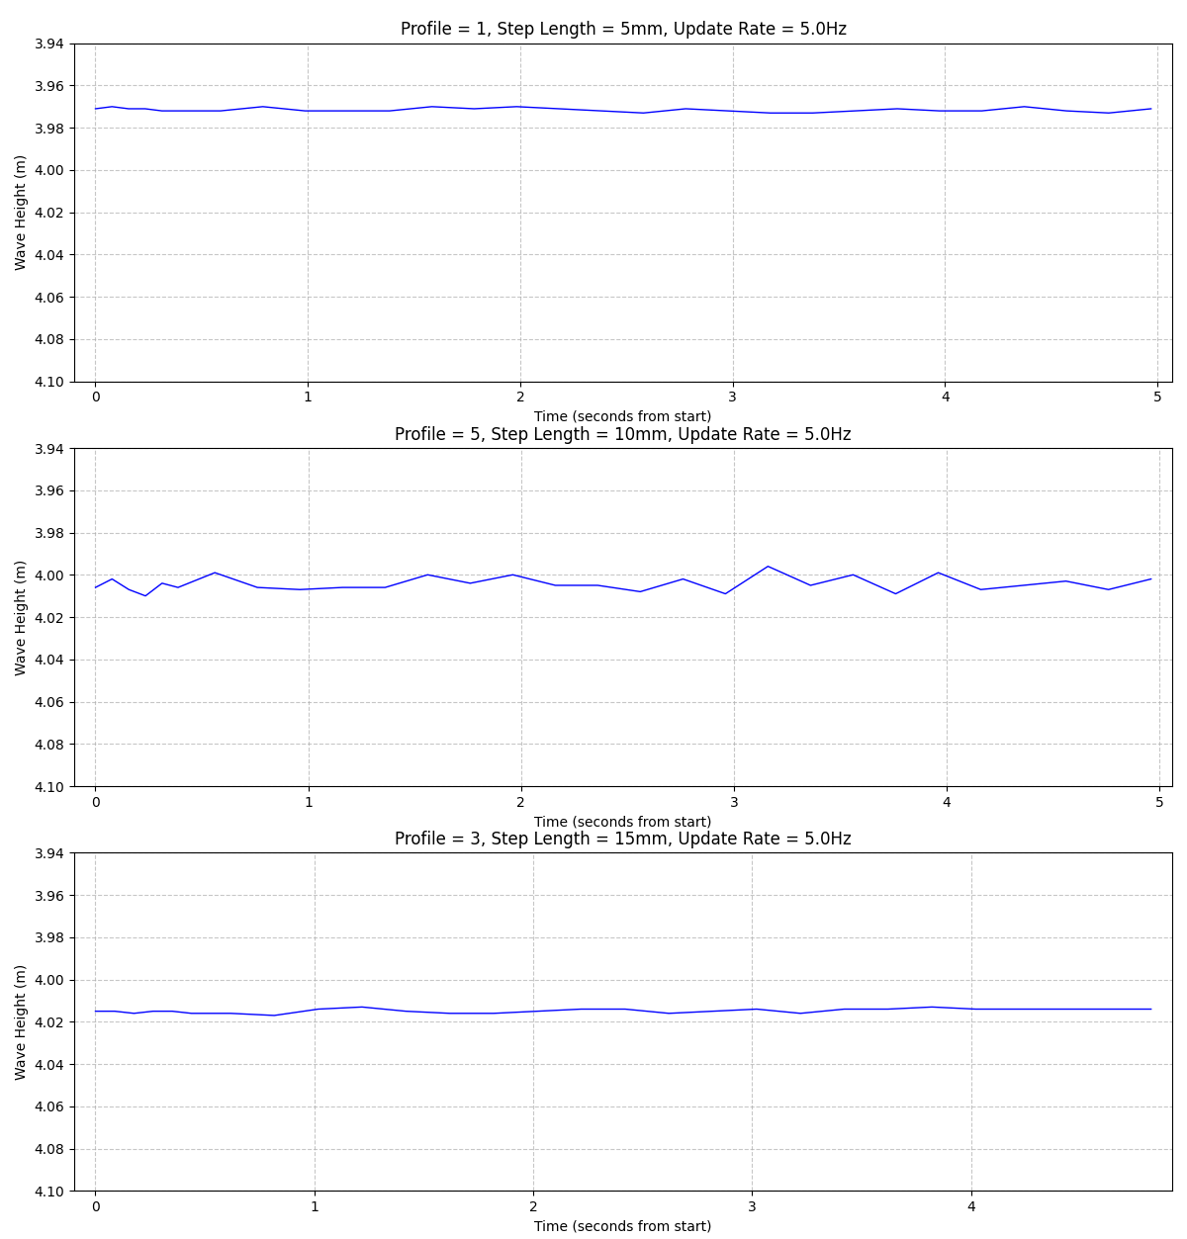
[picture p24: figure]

Figure 5. First five seconds of data collection for Tests 3, 5, and 7 (only varying profile)

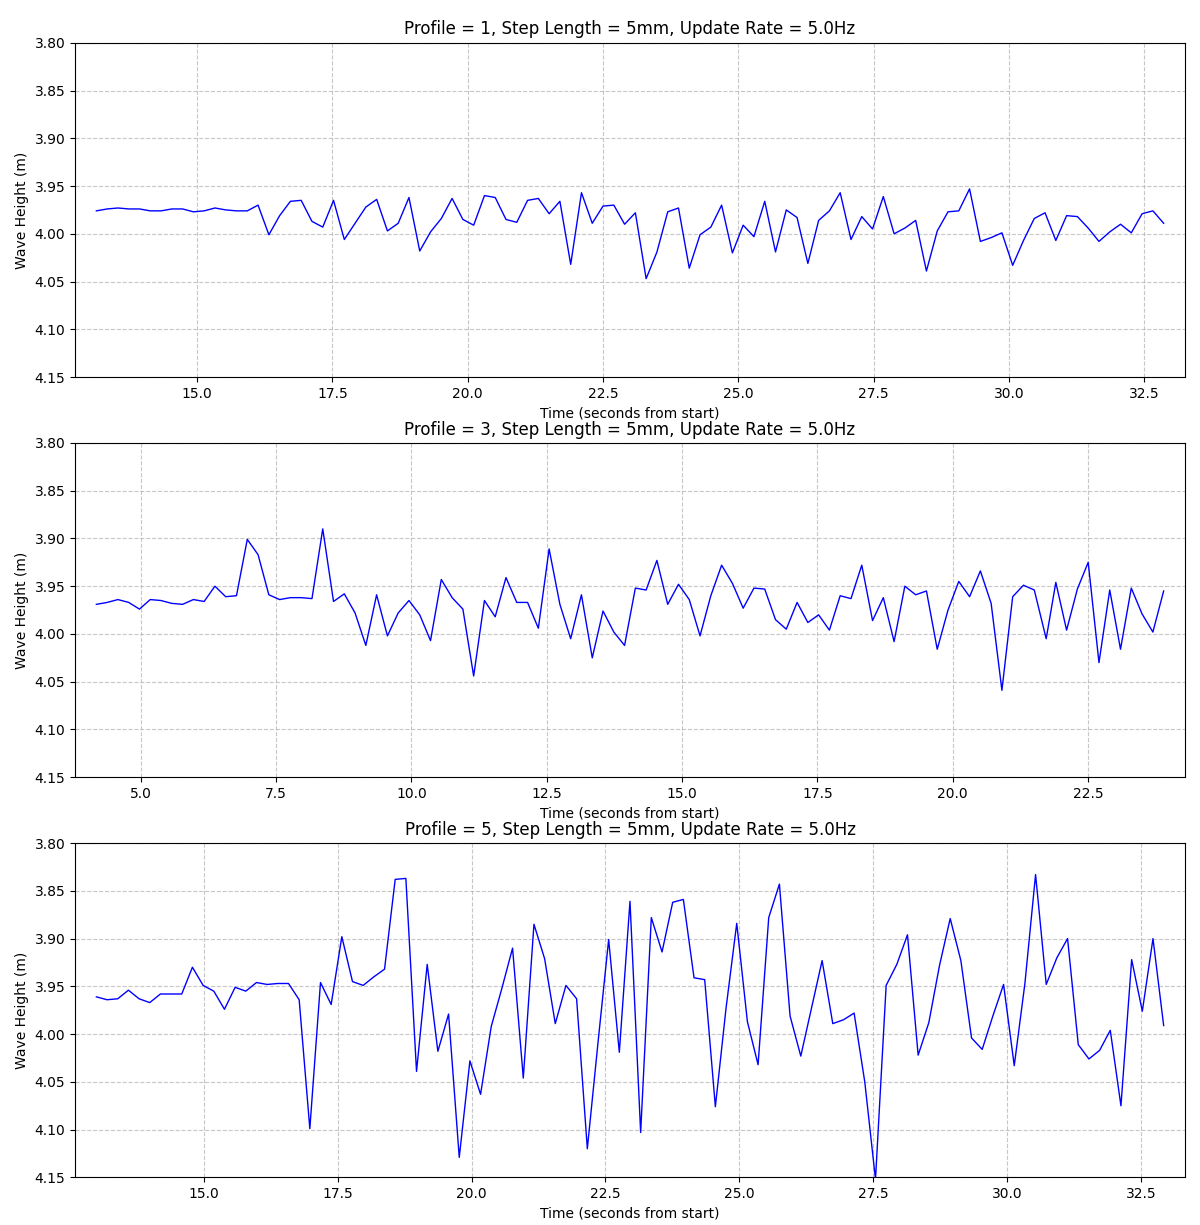
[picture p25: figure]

Figure 6. First bucket-hoisting portion of Tests 3, 1, and 2 (only varying profile); larger profiles resulted in much higher noise and less accurate measurements

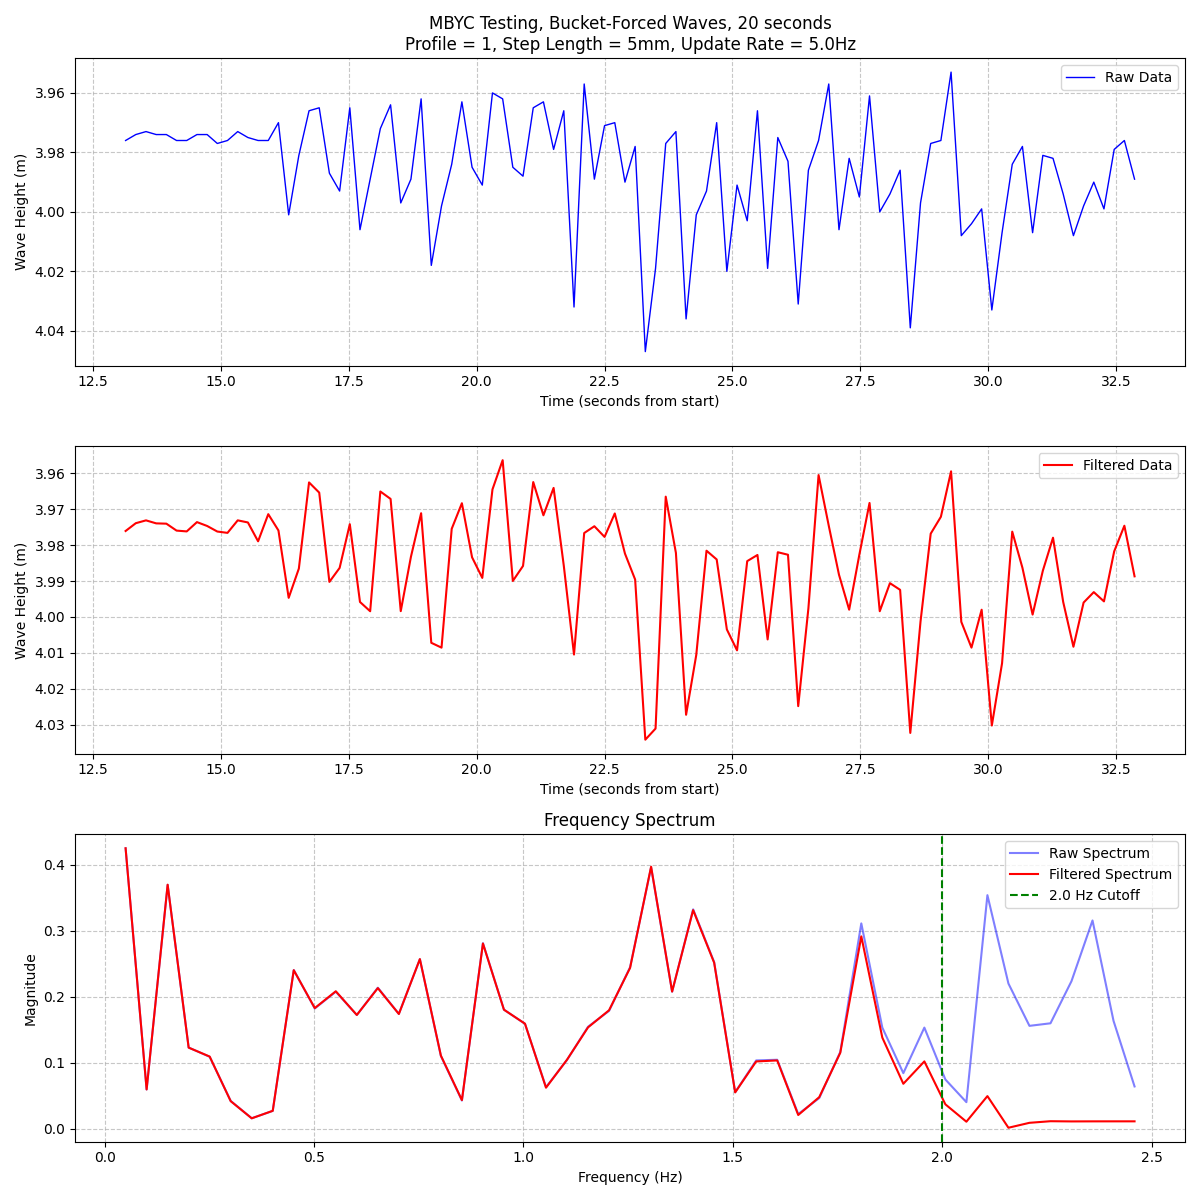
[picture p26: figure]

Figure 7. Frequency analysis of portion of Test 3 (profile = 1); large spikes between 1-2Hz showing that the waves were accurately recorded

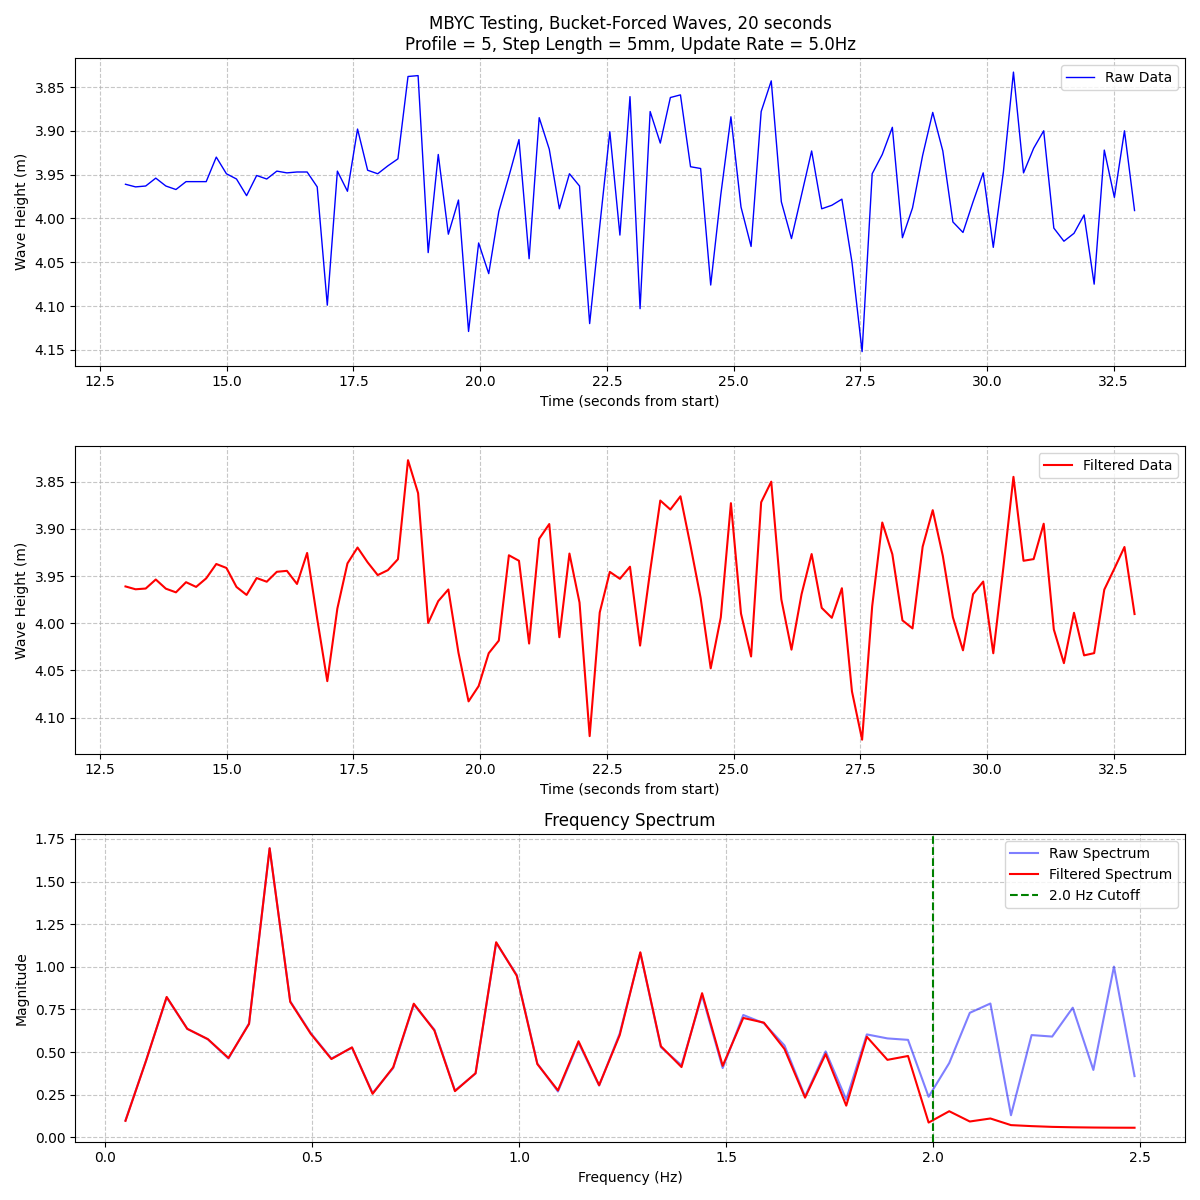
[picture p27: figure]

Figure 8. Frequency analysis of Test 2 (profile = 5); much less significant spikes between 1-2Hz, showing that the waves were not recorded as accurately as the profile=1 test

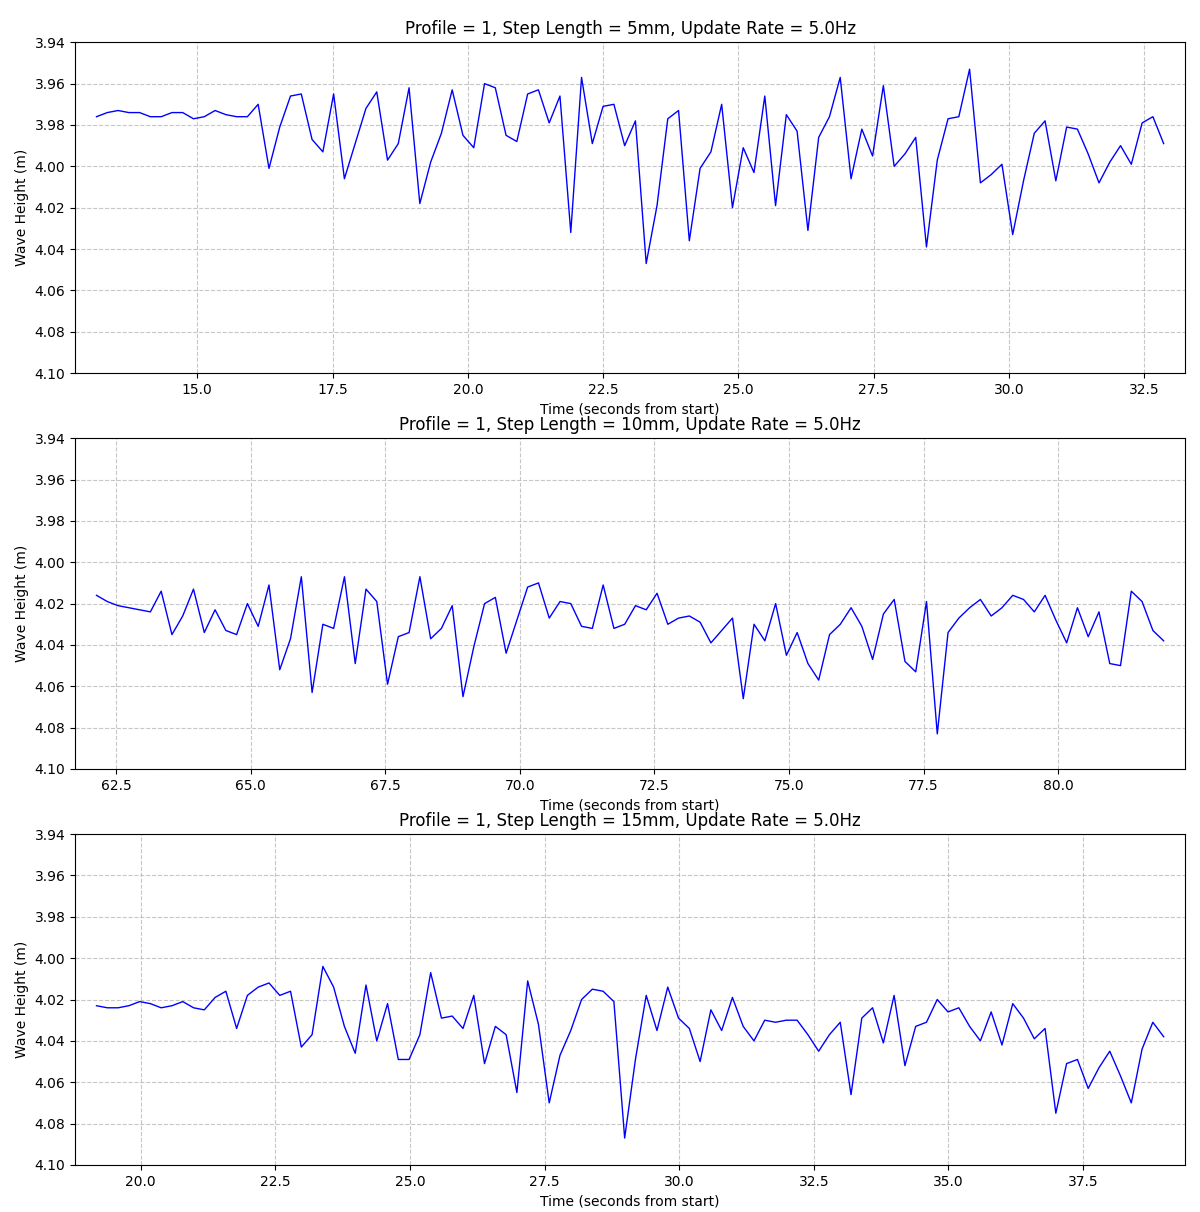
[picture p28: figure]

Figure 9. First bucket-hoisting portion of Tests 3, 6, and 9 (only varying step length); little difference between test results


Figure 10. Portion of Test 6 (5Hz update rate), waves visible but with lower temporal resolution


Figure 11. Portion of Test 11 (10Hz update rate); waves visible, with low-pass-filtered data giving much higher temporal resolution


Figure 12. All test data collected at the MBYC, concatenated, measured from initial testing time

Future Plans and Conclusion

Performing the testing at the MBYC was critical for optimizing the settings of the radar unit and for identifying several bugs in the code (file naming issue, GPS parsing error, etc.). These bugs will be fixed before the next field test is performed.

The following features are planned to be implemented on the radar unit before the next field test:

- Measure and account for the elevation of the radar unit as measured by the GPS receiver
- Implement low-power improvements to decrease power consumption
- Rework the code to use multitasking and to improve the SD card data writing process
- Characterize the power draw from each component (ESP32, STM32/radar, GPS) to further reduce power consumption

After these features are implemented, additional features (such as automatic range setting, which will improve power consumption, maximum update rate, and ease of deployment) are planned.

Finally, contact has been made with researchers at MBARI to deploy the radar unit at their Moss Landing facility during the King Tides event on November 15-17th, 2024. I will be in the Monterey Bay area that weekend and am in the process of organizing the deployment of the radar unit to collect tide data over a (unbroken) two-day period. This testing will be a fantastic test of long-term deployment in a controlled environment. The unit will be deployed in a similar fashion to the MBYC testing, except with the unit being enclosed in a waterproof container (similar to the current sonar implementation by Dr. Lee’s students).

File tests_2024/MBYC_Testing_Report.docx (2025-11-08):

Morro Bay Yacht Club Testing Report

Jakob Frabosilio, Student Assistant
Cal Poly SLO Mechanical Engineering Department
11/4/2024

Summary

The radar unit was tested at the Morro Bay Yacht Club on 10/27. The results show that small waves (1-2Hz, 2-10cm peak-to-peak) can be accurately measured on still water given proper configuration of the radar; Figure 0 shows a highlight of the test results. Additionally, the water level height decreasing with the tide was clear over the course of data collection; tide data can be accurately measured with the radar unit in its present form.

The testing was critical for finding optimal settings for the radar unit configuration and for identifying bugs in the firmware implementation. Future testing is planned at the Monterey Bay Aquarium Research Institute (MBARI) in Moss Landing from Nov. 15-17th (King Tides event) to test the long-term data collection of the radar unit.


Figure 0. Best results from MBYC testing; profile = 1, update rate = 10Hz

Introduction

On Sunday, October 27th, the low-cost water level gauge (“radar unit”) was tested at the Morro Bay Yacht Club with Dr. John Ridgely and Dr. Serena Lee. The purpose of the testing was to determine if small, rapid displacements in the water could be detected by the radar unit from a considerable distance away.

The radar unit was attached to an elevated dock approximately 4m above the surface of the water, sticking out approximately 50cm from the edge of the dock. The unit was powered using a 25W solar panel and a 5V solar power battery bank to ensure no power loss. The final implementation will use a solar panel with considerably less wattage – this panel was used for convenience. See Figure 1 for an image of the radar unit in its testing position.

Due to the still nature of the water below the dock (inside of a harbor on a windless day, protected from external waves by a floating dock), a bucket was attached to the end of a rope and was used to create controlled waves. The bucket was partially filled with water and was hoisted up and down repeatedly at a regular interval to create waves of a relatively known amplitude and frequency (roughly 2-10cm peak-to-peak amplitude and 1-2Hz frequency). See Figure 2 for an image of the bucket in the test environment. Note that some of the waves created by the bucket can be seen in the background of the image.


Figure 1. Radar unit suspended over the water surface, attached to the deck of the Morro Bay Yacht Club


Figure 2. Bucket and rope in foreground, used for controlling waves, with radar unit and waves in the background

Test Plan and Procedure

After an initial set-up and calibration period to ensure good measurements, a series of tests were performed to determine the optimal radar configuration settings. Three different settings were varied throughout the testing:

- Maximum Profile (1, 3, 5)
  - Determines the duration and shape of the radar burst. A higher profile setting (5) increases the signal-to-noise ratio but decreases the maximum update rate.
  - Additionally, higher profile settings can make it difficult to distinguish between multiple objects in a scene, as seen in Figure 3.
- Maximum Step Length (5mm, 10mm, 15mm)
  - Determines the maximum distance between radar measurements. A lower maximum step length results in more measurements taken for a given measurement range, increasing the power consumption and decreasing the update rate, but returning more accurate measurements for small displacements.
  - The radar works by sending out pulses and measuring the return in discrete intervals. If the start range of the radar is set to 1m and the end range is set to 2m, the step length determines how that range is subdivided. For a max step length of 100mm, the radar would test the return strength at 1m, 1.1m, 1.2m, etc. until it hits 2m.
  - The radar unit uses phase data to interpolate between these measurements. If an object is located at 1.05m, the radar unit can still detect it using a step length of 100mm, despite the object not appearing directly at a measured distance.
- Update Rate (5Hz, 10Hz)
  - Determines how often measurements are taken. Limited by other configuration settings (profile, step length, measurement range), and increases power draw as it rises.
  - Higher update rates are required to measure waves with higher frequencies. To measure waves with a frequency of 2Hz, a minimum 4Hz update rate is required. Generally, higher frequencies produce cleaner data in this application.


Figure 3. Mock data for different maximum profile settings, three objects in measurement range; Profile=2 captures all three objects, while Profile=3 incorrectly combines the first and second object

Note that there are other configuration settings beyond these three for the radar unit; these three are simply the most important to tune for this application, especially given the power consumption requirements.

A total of 12 tests were conducted using combinations of the above settings. The table below summarizes the configuration for each test, as well as its start time.

Test Number | Start Time (PDT) | Max Profile | Max Step Length | Update Rate
1 | 12:57pm | 3 | 5mm | 5Hz
2 | 1:00pm | 5 | 5mm | 5Hz
3 | 1:04pm | 1 | 5mm | 5Hz
4 | 1:09pm | 3 | 10mm | 5Hz
5 | 1:12pm | 5 | 10mm | 5Hz
6 | 1:16pm | 1 | 10mm | 5Hz
7 | 1:22pm | 3 | 15mm | 5Hz
8 | 1:27pm | 5 | 15mm | 5Hz
9 | 1:31pm | 1 | 15mm | 5Hz
10 | 1:38pm | 5 | 10mm | 10Hz
11 | 1:45pm | 1 | 10mm | 10Hz
12 | 1:49pm | 3 | 10mm | 10Hz

For each test, the following procedure was carried out:

- Place the bucket in the water approximately 3m from the center of the radar unit, measured horizontally
- Wait until the water below the sensor is still before beginning the test
- After starting data collection, wait approximately 10-20 seconds to collect still water readings (no waves, minimal noise; flat surface)
- Raise and lower the bucket approximately 20cm (peak-to-peak) using the rope at a rate of 1-2Hz for approximately 20 seconds
- Wait for the water to settle, approximately 20 seconds
- Raise and lower the bucket as before, but with a greater amplitude (and more splashing / noise)
- Continue collecting data for 20 seconds after the second round of bucket hoisting

Figure 4 shows the results of an average test as measured by the radar unit. Note that the y-axis is flipped; the radar unit currently measures the distance from the unit’s lens to the surface of the water, so a wave with positive displacement (or a rising tide) means that the measured distance decreases. In the future, the elevation data of the radar unit will be incorporated to convert the relative-distance measurements into absolute height measurements (relative to average sea level).


Figure 4. Test 6 full results from radar unit

Results and Analysis

All tests produced similar results for the first portion of the procedure (measuring only the still water) – the average noise in these readings is around 1cm peak-to-peak for all tests. Figure 5 shows the first five seconds of data collection for three different tests. The profile, step length, and update rate have little-to-no effect on the noise floor for still water.

To determine which settings are most “optimal” or “accurate” is difficult, given that the true wave amplitude and frequency were only estimated visually. However, a few key items are known that will aid in analysis:

- The true wave frequency (waves created by the bucket hoisting up and down) is between 1-2Hz; if the primary frequencies in the radar data are between these values, then the wave is likely being recorded properly.
- The true wave amplitude is roughly between 2-10cm peak-to-peak; if the amplitude of the measured waves is significantly higher than this range, then there is likely significant noise in the measurements.

The maximum profile appears to have a large impact on the quality of the measurements. Figure 6 shows a comparison between profile settings of 1, 3, and 5; as the profile increases, the noise during these wave measurements increases dramatically. Note that the profile=5 test measured wave amplitudes much higher than 10cm peak-to-peak.

Additionally, a frequency analysis of these tests shows that the true wave frequency (between 1-2Hz) is much more prevalent in the profile=1 test than the profile=5 test; see Figures 7 and 8 respectively for these tests. Given these results (and the fact that higher profiles increase the power consumption and lower the maximum update rate significantly), it is recommended that the profile be set as low as possible.

The step length did not appear to have a large impact on the accuracy of the results. Figure 9 shows a comparison of three different step length settings with profile = 1. The wave amplitudes and frequency components are comparable for the three tests. Future testing, with a way to verify the true height of the waves, is required to determine optimal settings for the step length. At present, it is recommended that the step length be set as high as possible to decrease power consumption and increase the maximum update rate.

The update rate has a large impact on the quality of the results, given the wave frequency of 1-2Hz. An update rate of 5Hz was slightly low to cleanly capture the waves created by the bucket; increasing the rate to 10Hz yielded much better results. Compare Figures 10 and 11; the higher update rate (combined with a low-pass filter to remove high-frequency noise components) produced very clear measurements of the bucket-forced waves. It is recommended to set the update rate as high as possible to accurately capture the profile of high-frequency waves. 10Hz appears to be a good compromise between power consumption and accuracy.

All testing was conducted over the course of an hour; on the day of testing, the high tide was around 9am and low tide was around 2pm. The estimated water level drop across the testing period, using tide data from tide-forecast.com, was approximately 0.12m. Figure 12 shows all of the testing data concatenated, with the tide drop clearly present.

The lack of a smooth line is due to the changing configuration of the radar for each test; changing the measurement profile affects the “average” readings of the water level. For the highest profile (Tests 2, 5, 8, and 10), the average water level measured was slightly higher than adjacent tests. With higher profiles, more energy is sent in the radar burst; it is assumed that these higher energy levels reflect off the surface of the water earlier (with lower profile bursts penetrating the water slightly more). The tide data can be easily measured using any settings of the radar unit, but the profile slightly affects the average water height reading. Further testing and improved implementation are required to accurately characterize this behavior.


Figure 5. First five seconds of data collection for Tests 3, 5, and 7 (only varying profile)


Figure 6. First bucket-hoisting portion of Tests 3, 1, and 2 (only varying profile); larger profiles resulted in much higher noise and less accurate measurements


Figure 7. Frequency analysis of portion of Test 3 (profile = 1); large spikes between 1-2Hz showing that the waves were accurately recorded


Figure 8. Frequency analysis of Test 2 (profile = 5); much less significant spikes between 1-2Hz, showing that the waves were not recorded as accurately as the profile=1 test


Figure 9. First bucket-hoisting portion of Tests 3, 6, and 9 (only varying step length); little difference between test results


Figure 10. Portion of Test 6 (5Hz update rate), waves visible but with lower temporal resolution


Figure 11. Portion of Test 11 (10Hz update rate); waves visible, with low-pass-filtered data giving much higher temporal resolution


Figure 12. All test data collected at the MBYC, concatenated, measured from initial testing time

Future Plans and Conclusion

Performing the testing at the MBYC was critical for optimizing the settings of the radar unit and for identifying several bugs in the code (file naming issue, GPS parsing error, etc.). These bugs will be fixed before the next field test is performed.

The following features are planned to be implemented on the radar unit before the next field test:

- Measure and account for the elevation of the radar unit as measured by the GPS receiver
- Implement low-power improvements to decrease power consumption
- Rework the code to use multitasking and to improve the SD card data writing process
- Characterize the power draw from each component (ESP32, STM32/radar, GPS) to further reduce power consumption

After these features are implemented, additional features (such as automatic range setting, which will improve power consumption, maximum update rate, and ease of deployment) are planned.

Finally, contact has been made with researchers at MBARI to deploy the radar unit at their Moss Landing facility during the King Tides event on November 15-17th, 2024. I will be in the Monterey Bay area that weekend and am in the process of organizing the deployment of the radar unit to collect tide data over a (unbroken) two-day period. This testing will be a fantastic test of long-term deployment in a controlled environment. The unit will be deployed in a similar fashion to the MBYC testing, except with the unit being enclosed in a waterproof container (similar to the current sonar implementation by Dr. Lee’s students).

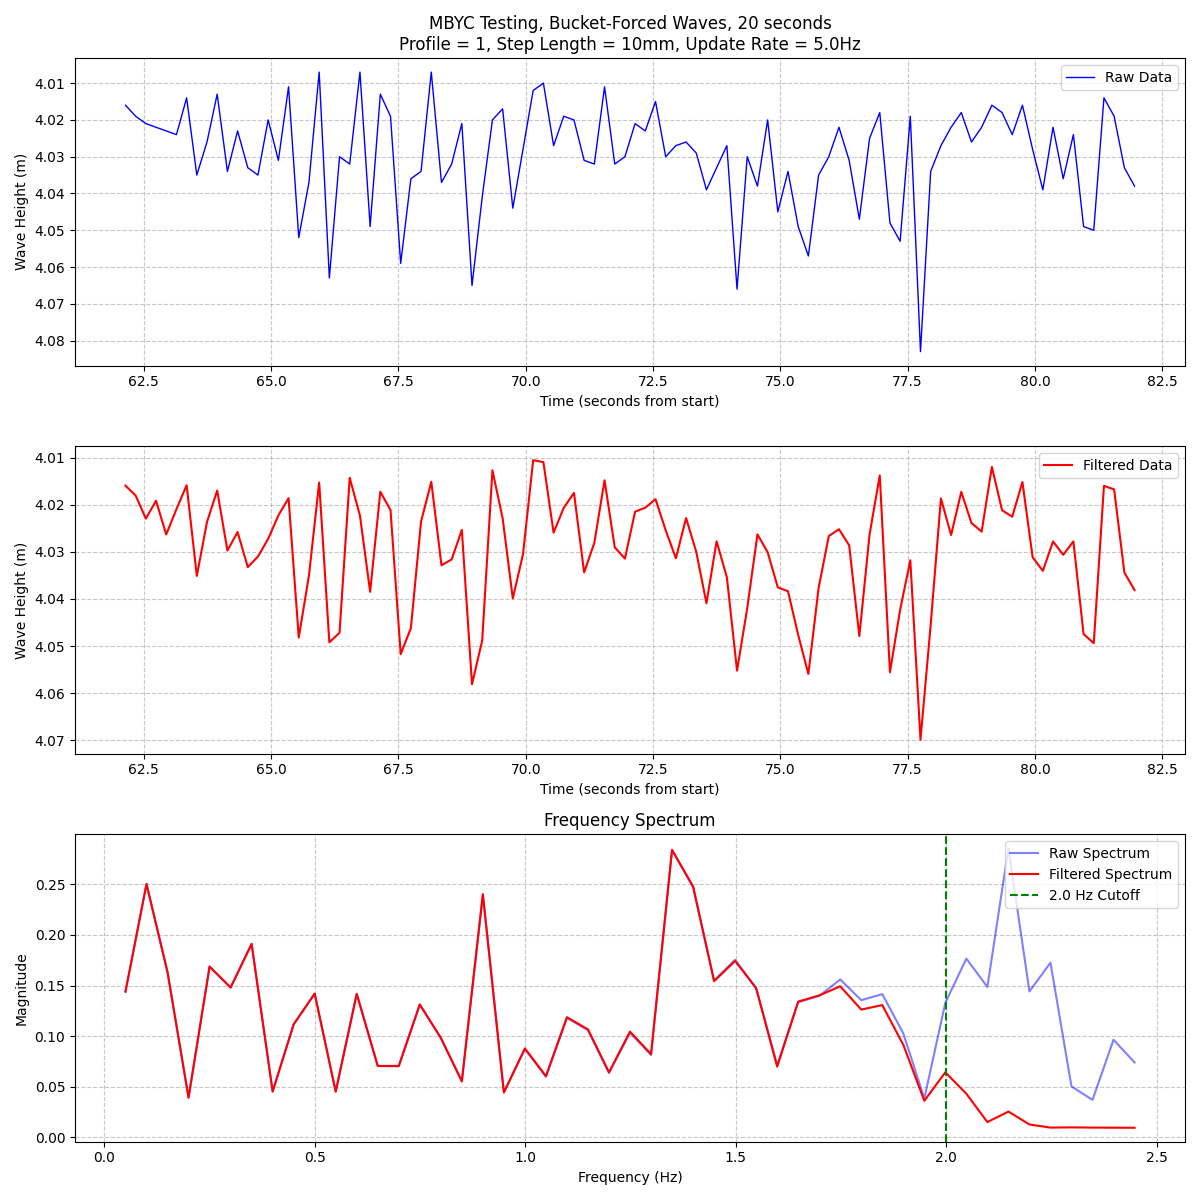
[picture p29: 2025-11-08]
tests_2024/testing_pics/mbyc/p1l4u5_20.png

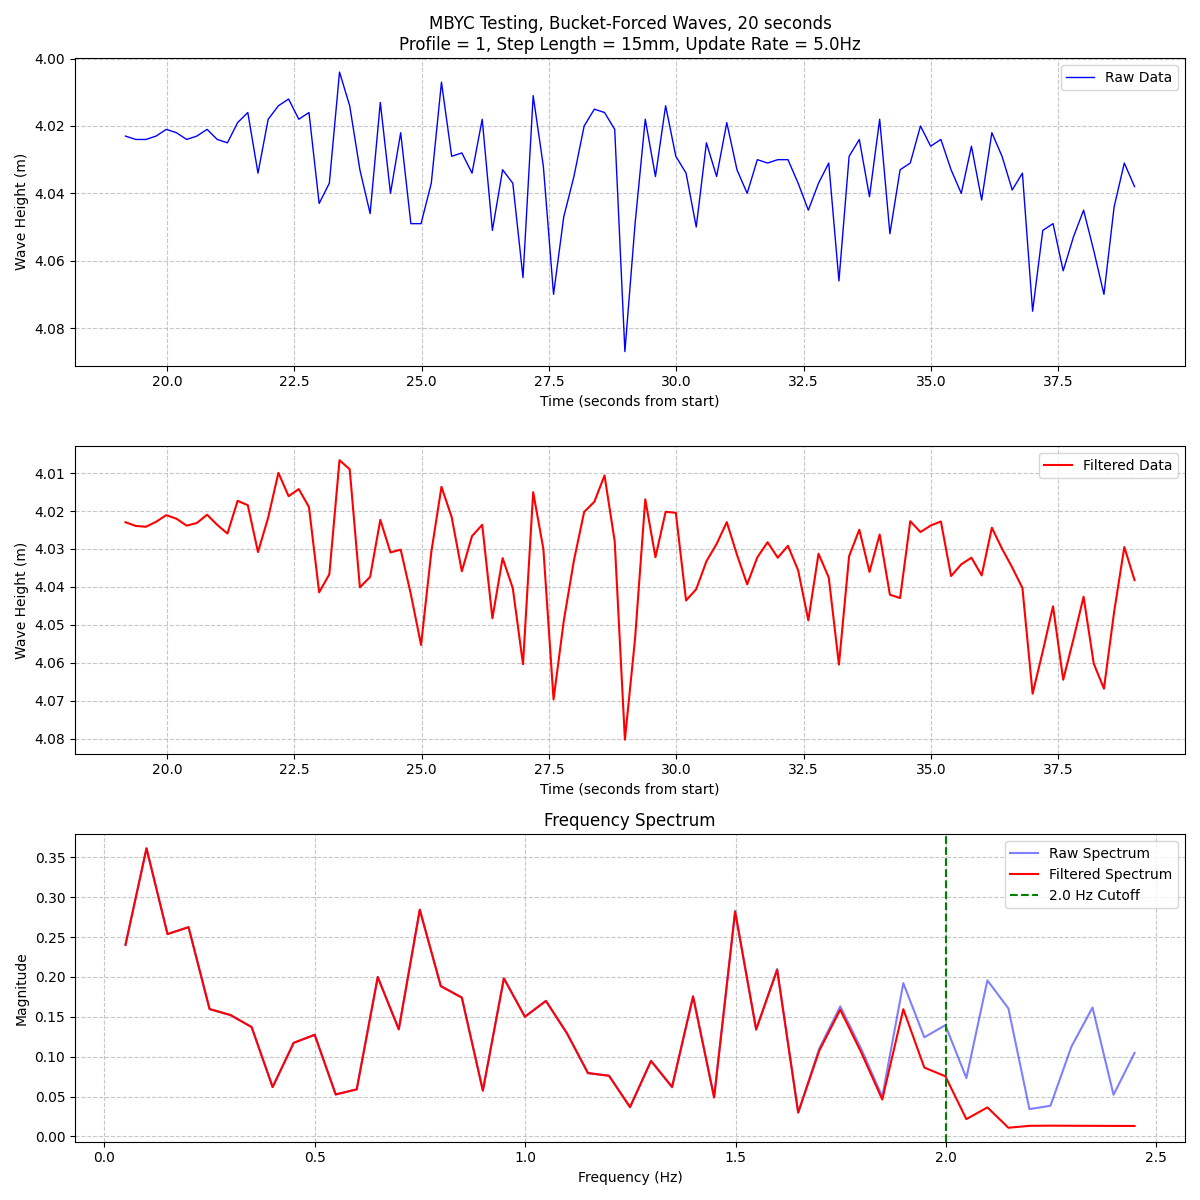
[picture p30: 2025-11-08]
tests_2024/testing_pics/mbyc/p1l6u5_20.png

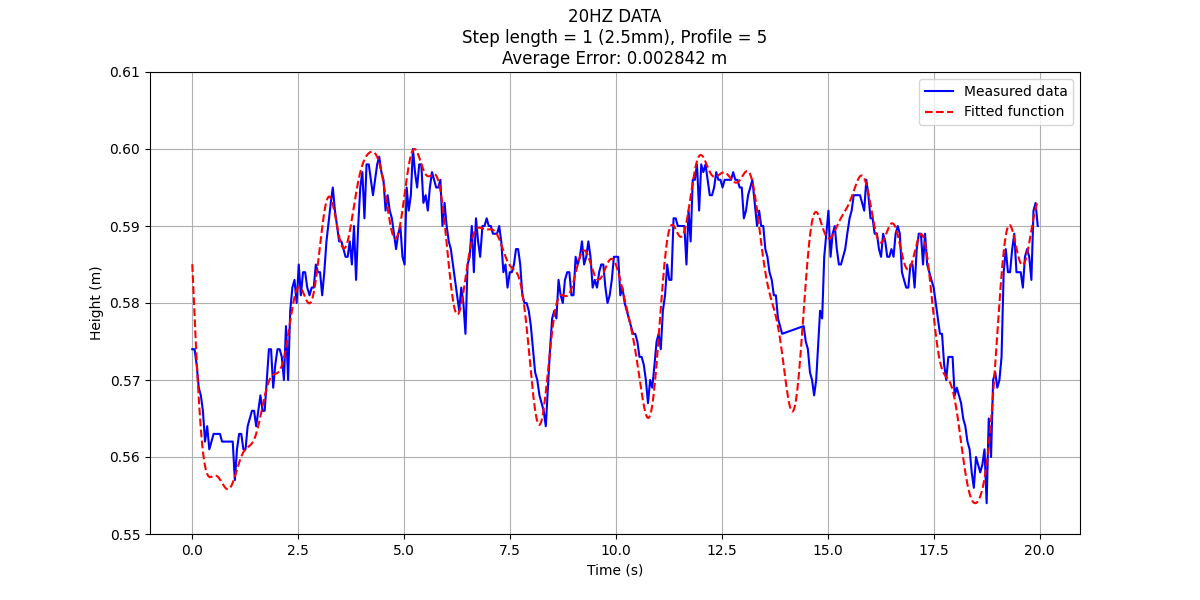
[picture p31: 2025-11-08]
tests_2024/testing_pics/Fo-SHIP/20hz.png

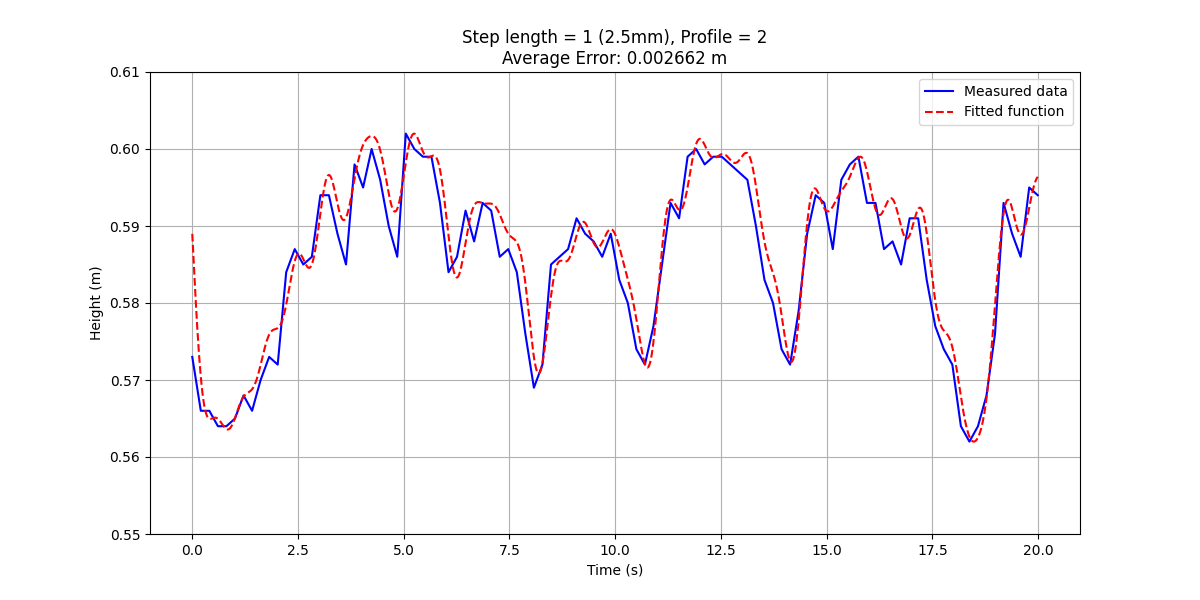
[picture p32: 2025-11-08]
tests_2024/testing_pics/Fo-SHIP/l1p2.png

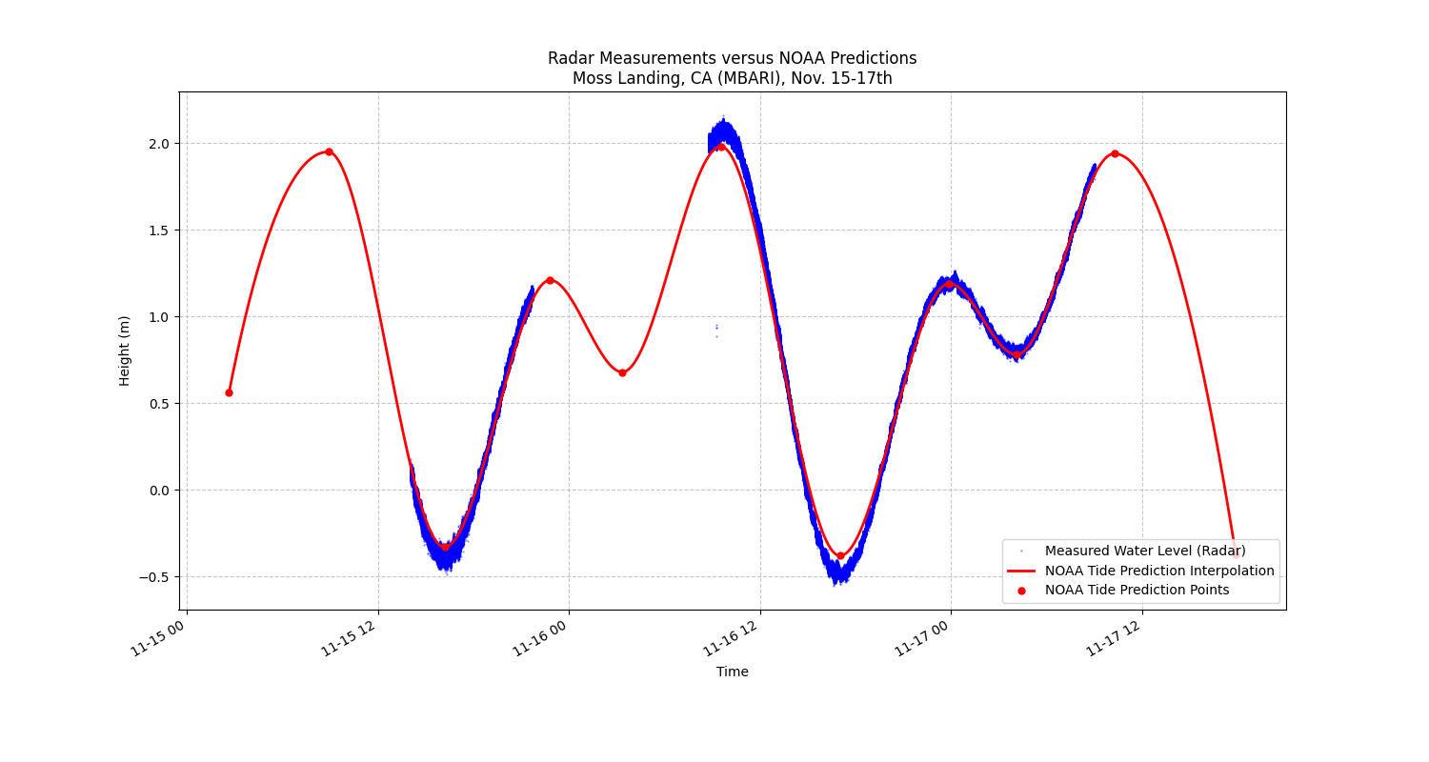
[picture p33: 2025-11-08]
tests_2024/testing_pics/mbari_first_look.png

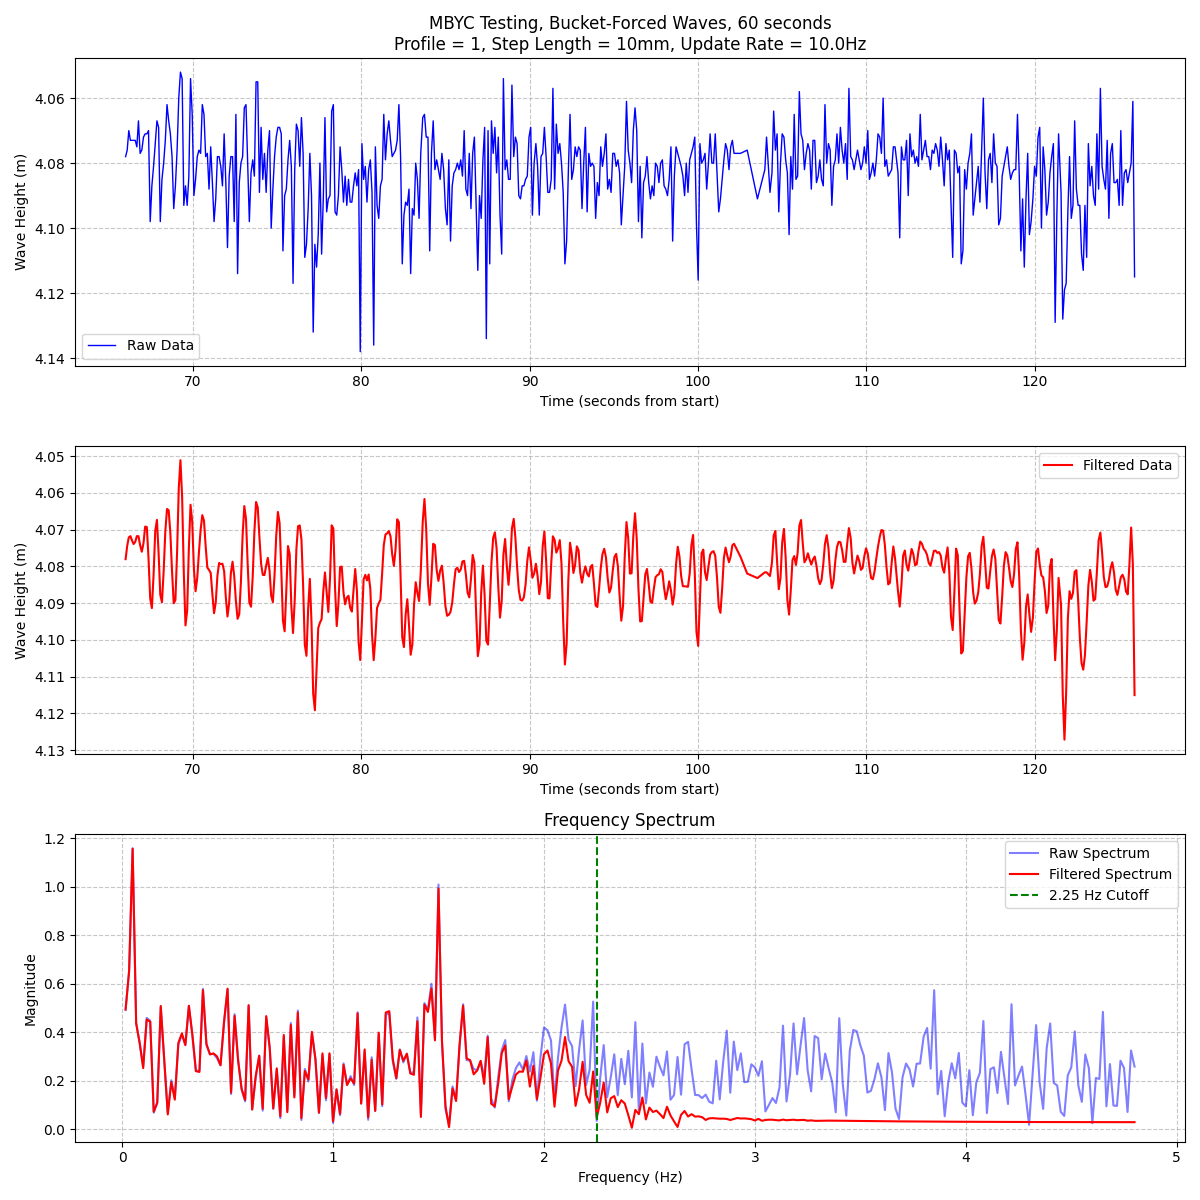
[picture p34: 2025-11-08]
tests_2024/testing_pics/mbyc/p1l4u10_60.png

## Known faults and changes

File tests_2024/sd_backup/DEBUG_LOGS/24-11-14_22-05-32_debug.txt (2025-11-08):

ESP32: Loaded config file.
ESP32: Configuration loaded from SD card.
ESP32: Loaded previous GPS coordinates: 38°05'04.69"N 122°34'16.59"W
STM32: M807
ESP32: Sending config to STM...
ESP32: Sent from ESP32:     00.20,00.80,10.0,04,3,20.0,0,0.50,0,00.2
ESP32: Received from STM32: M807
ESP32: Received from STM32: M807
ESP32: Received from STM32: M807
ESP32: Received from STM32: 00.20,00.80,10.0,04,3,20.0,0,0.50,0,00.2
ESP32: Received from STM32: M808
STM32: Configuration received and loaded onto radar sensor.
STM32: 
STM32: 00:00:07.398 (I) (detector_distance) Detector Distance Config
STM32: 00:00:07.398 (I) (detector_distance) start_m: 0.200000
STM32: 00:00:07.399 (I) (detector_distance) end_m: 0.800000
STM32: 00:00:07.400 (I) (detector_distance) max_step_length: 4
STM32: 00:00:07.401 (I) (detector_distance) max_profile: PROFILE_3
STM32: 00:00:07.402 (I) (detector_distance) close_range_leakage_cancellation: false
STM32: 00:00:07.403 (I) (detector_distance) signal_quality: 20.000000
STM32: 00:00:07.404 (I) (detector_distance) threshold_method: C00:00:07.409 (I) 00:00:07.410 (I) (detector_distance) Offset00:00:07.41
STM32: 5 (I) (config) inter_sweep_idle_state: READY
STM32: 00:00:07.416 (I) (con00:00:07.423 (I) (config)     enable_loopback  : true
STM32: 00:00:07.00:00:07.429 (I) (config) double_buffering: false
STM32: 00:00:07.430 (I) (config) inter_frame_idle_state: DEEP_SLEEP
STM32: 00:00:07.431 (I)00:00:07.440 (I) (detector_dista00:00:07.441 00:00:07.445 (I) (config00:00:07.446 (I) (config) inter_sweep_idle
STM32: _state: R00:00:07.452 (I) (config)     phase_enhancement: true
STM32: 00:00
STM32: M114
STM32: DATA_START
ESP32: ---------- ---------- ---------- ---------- -------- ---------- ---------- ---------- ----------
ESP32: ---------- ---------- ---------- ---------- NEW DATA ---------- ---------- ---------- ----------
ESP32: ---------- ---------- ---------- ---------- -------- ---------- ---------- ---------- ----------
ESP32: First Data File Since Powering On: True
ESP32: Data File: /DATA/24-11-14_22-05-40_data.txt
ESP32: Start Time: [24/11/14 22:05:40.916]
ESP32: Location: 38°05'04.69"N 122°34'16.59"W
ESP32: Elevation: 54.8
ESP32: Start of range: 0.20 m
ESP32: End of range: 0.80 m
ESP32: Update rate: 10.0 Hz
ESP32: Maximum step length: 4 (10.0 mm)
ESP32: Maximum profile: 3
ESP32: Signal quality: 20.0
ESP32: Reflector shape: 0 (0: generic, 1: planar)
ESP32: Threshold sensitivity: 0.50
ESP32: True update rate: 0.2 Hz
ESP32: Text width: 40 characters
ESP32: ---
STM32: M
STM32: 
STM32: Stopping radar...
STM32: Process will take approximately 1.3 seconds.
STM32: 
STM32: Radar stopped.
STM32: 
ESP32: --- CONFIGURATION MENU ---
ESP32: Send one of the below characters to change that configuration setting.
ESP32: Changes will be saved upon exiting menu.
ESP32: S: Change the start of the measurement range. Affects power consumption and update rate.
ESP32:    Current value: 00.20 m
ESP32: E: Change the end of the measurement range. Affects power consumption and update rate.
ESP32:    Current value: 00.80 m
ESP32: U: Change the update rate. Affects power consumption.
ESP32:    Current value: 10.0 Hz
ESP32: L: Change the maximum step length of the measurements. Affects power consumption, update rate, and resolution.
ESP32:    Current value: 04 (10.0 mm)
ESP32: P: Change the maximum measurement profile. Affects power consumption, update rate, and accuracy.
ESP32:    Current value: 3
ESP32: Q: Change the signal quality. Affects power consumption, update rate, and accuracy.
ESP32:    Current value: 20.0
ESP32: R: Change the reflector shape.
ESP32:    Current value: 0 (0: generic, 1: planar)
ESP32: T: Change the threshold sensitivity. Affects accuracy.
ESP32:    Current value: 0.50
ESP32: W: Set the text width for the Bluetooth UART output.
ESP32:    Current value: 040 characters
ESP32: A: Measure the actual update rate.
ESP32:    True update rate: 00.2 Hz
ESP32: B: Print to Bluetooth in serial plotter mode for two minutes.
ESP32:    Useful for tuning settings with visual indicators.
ESP32:    Recommended to use Arduino IDE serial plotter.
ESP32: X: Exit the menu.
ESP32: 
Input: r
ESP32: 
ESP32: Sets the reflector shape. Current value: 0
ESP32: Format: X
ESP32:  Input must match format exactly.
ESP32:  Enter "1" to use planar reflector shape.
ESP32:  Enter "0" to use generic reflector shape.
ESP32: Notes:
ESP32:  Planar reflector shape should be used for determining the distance to flat objects like water surfaces,
ESP32:  sheets of metal, walls, and more.
ESP32:  Generic reflector shape should be used for determining the distance to any other objects.
ESP32: Example:
ESP32:  The radar is installed on the edge of a pier above a body of water.
ESP32:  Planar reflector shape should be used, and the user would enter "1" with no quotes.
ESP32: 
Input: 1
ESP32: 
ESP32: Reflector shape set to 1
ESP32: Is this the desired value? Type Y for yes, N for no.
ESP32: 
Input: y
ESP32: 
ESP32: Value saved.
ESP32: 
ESP32: --- CONFIGURATION MENU ---
ESP32: Send one of the below characters to change that configuration setting.
ESP32: Changes will be saved upon exiting menu.
ESP32: S: Change the start of the measurement range. Affects power consumption and update rate.
ESP32:    Current value: 00.20 m
ESP32: E: Change the end of the measurement range. Affects power consumption and update rate.
ESP32:    Current value: 00.80 m
ESP32: U: Change the update rate. Affects power consumption.
ESP32:    Current value: 10.0 Hz
ESP32: L: Change the maximum step length of the measurements. Affects power consumption, update rate, and resolution.
ESP32:    Current value: 04 (10.0 mm)
ESP32: P: Change the maximum measurement profile. Affects power consumption, update rate, and accuracy.
ESP32:    Current value: 3
ESP32: Q: Change the signal quality. Affects power consumption, update rate, and accuracy.
ESP32:    Current value: 20.0
ESP32: R: Change the reflector shape.
ESP32:    Current value: 1 (0: generic, 1: planar)
ESP32: T: Change the threshold sensitivity. Affects accuracy.
ESP32:    Current value: 0.50
ESP32: W: Set the text width for the Bluetooth UART output.
ESP32:    Current value: 040 characters
ESP32: A: Measure the actual update rate.
ESP32:    True update rate: 00.2 Hz
ESP32: B: Print to Bluetooth in serial plotter mode for two minutes.
ESP32:    Useful for tuning settings with visual indicators.
ESP32:    Recommended to use Arduino IDE serial plotter.
ESP32: X: Exit the menu.
ESP32: 
Input: a
ESP32: 
ESP32: Sending config to STM...
ESP32: Sent from ESP32:     00.20,00.80,10.0,04,3,20.0,1,0.50,1,00.2
ESP32: Received from STM32: M807
ESP32: Received from STM32: M807
ESP32: Received from STM32: M807
ESP32: Received from STM32: M807
ESP32: Received from STM32: M807
ESP32: Received from STM32: M807
ESP32: Received from STM32: M807
ESP32: Received from STM32: M807
ESP32: Received from STM32: 00.20,00.80,10.0,04,3,20.0,1,0.50,1,00.2
ESP32: Received from STM32: M808
STM32: Configuration received and loaded onto radar sensor.
STM32: 
ESP32: Testing actual update rate...
STM32: 00:01:20.593 (I) (detector_distance) Detector Distance Config
STM32: 00:01:20.593 (I) (detector_distance) start_m: 0.200000
STM32: 00:01:20.594 (I) (detector_distance) end_m: 0.800000
STM32: 00:01:20.595 (I) (detector_distance) max_step_length: 4
STM32: 00:01:20.596 (I) (detector_distance) max_profile: PROFILE_3
STM32: 00:01:20.597 (I) (detector_distance) close_range_leakage_cancellation: false
STM32: 00:01:20.598 (I) (detector_distance) signal_quality: 20.000000
STM32: 00:01:20.599 (I) (detector_distance) threshold_method: 000:00:01:20.605 (I) (detector_distance) Offset Calibration C00:01:20.61
STM32: 0 (I) (config) inter_sweep_idle_state: READY
STM32: 00:01:20.611 (I) (con00:01:20.618 (I) (config)     enable_loopback  : true
STM32: 00:01:20.00:01:20.624 (I) (config) double_buffering: false
STM32: 00:01:20.625 (I) (config) inter_frame_idle_state: DEEP_SLEEP
STM32: 00:01:20.626 (I)00:01:20.600:01:20.636 (I) (config) sweep_rat00:01:2000:01:20.641 (I) (config) inter_sweep_idle_state: READY
STM32: 00:01:20.6400:01:20.647 (I) (config)     phase_enhanceme00:01:20.648 (
STM32: [24/11/14 22:06:54.103] 0.531 m, 7.84
STM32: [24/11/14 22:06:54.116] 0.530 m, 7.72
STM32: [24/11/14 22:06:54.168] 0.530 m, 7.96
STM32: M814
STM32: [24/11/14 22:06:54.269] 0.531 m, 7.80
STM32: [24/11/14 22:06:54.369] 0.530 m, 7.90
STM32: [24/11/14 22:06:54.469] 0.531 m, 7.81
STM32: [24/11/14 22:06:54.570] 0.531 m, 7.91
STM32: [24/11/14 22:06:54.670] 0.531 m, 7.68
STM32: [24/11/14 22:06:54.771] 0.531 m, 7.81
STM32: [24/11/14 22:06:54.871] 0.531 m, 7.73
STM32: [24/11/14 22:06:54.972] 0.531 m, 7.69
STM32: [24/11/14 22:06:55.073] 0.531 m, 7.78
STM32: [24/11/14 22:06:55.173] 0.531 m, 7.85
STM32: [24/11/14 22:06:55.274] 0.530 m, 7.83
STM32: [24/11/14 22:06:55.374] 0.531 m, 7.83
STM32: [24/11/14 22:06:55.475] 0.531 m, 7.75
STM32: [24/11/14 22:06:55.575] 0.531 m, 7.80
STM32: [24/11/14 22:06:55.676] 0.531 m, 7.63
STM32: [24/11/14 22:06:55.776] 0.531 m, 7.74
STM32: [24/11/14 22:06:55.877] 0.531 m, 7.64
STM32: [24/11/14 22:06:55.978] 0.530 m, 7.72
STM32: [24/11/14 22:06:56.078] 0.530 m, 7.91
STM32: [24/11/14 22:06:56.178] 0.531 m, 7.78
STM32: [24/11/14 22:06:56.279] 0.531 m, 8.01
STM32: [24/11/14 22:06:56.379] 0.530 m, 7.60
STM32: [24/11/14 22:06:56.480] 0.530 m, 7.78
STM32: [24/11/14 22:06:56.580] 0.531 m, 7.89
STM32: [24/11/14 22:06:56.681] 0.531 m, 7.77
STM32: [24/11/14 22:06:56.781] 0.530 m, 7.75
STM32: [24/11/14 22:06:56.882] 0.531 m, 7.50
STM32: [24/11/14 22:06:56.982] 0.530 m, 7.95
STM32: [24/11/14 22:06:57.083] 0.531 m, 7.83
STM32: [24/11/14 22:06:57.183] 0.530 m, 7.86
STM32: [24/11/14 22:06:57.284] 0.531 m, 8.11
STM32: [24/11/14 22:06:57.384] 0.531 m, 7.85
STM32: [24/11/14 22:06:57.485] 0.531 m, 7.68
STM32: [24/11/14 22:06:57.585] 0.531 m, 7.73
STM32: [24/11/14 22:06:57.686] 0.531 m, 7.77
STM32: [24/11/14 22:06:57.786] 0.531 m, 7.85
STM32: [24/11/14 22:06:57.887] 0.530 m, 7.67
STM32: [24/11/14 22:06:57.987] 0.531 m, 7.76
STM32: [24/11/14 22:06:58.088] 0.531 m, 7.69
STM32: [24/11/14 22:06:58.188] 0.531 m, 7.79
STM32: [24/11/14 22:06:58.289] 0.531 m, 7.70
STM32: [24/11/14 22:06:58.389] 0.531 m, 7.69
STM32: [24/11/14 22:06:58.490] 0.531 m, 7.83
STM32: [24/11/14 22:06:58.590] 0.530 m, 7.78
STM32: [24/11/14 22:06:58.690] 0.531 m, 7.84
STM32: [24/11/14 22:06:58.791] 0.531 m, 7.67
STM32: [24/11/14 22:06:58.891] 0.531 m, 7.63
STM32: [24/11/14 22:06:58.992] 0.531 m, 7.79
STM32: [24/11/14 22:06:59.092] 0.531 m, 7.74
STM32: M815
STM32: 49
ESP32: Actual update rate measured as 9.9 Hz.
ESP32: --- CONFIGURATION MENU ---
ESP32: Send one of the below characters to change that configuration setting.
ESP32: Changes will be saved upon exiting menu.
ESP32: S: Change the start of the measurement range. Affects power consumption and update rate.
ESP32:    Current value: 00.20 m
ESP32: E: Change the end of the measurement range. Affects power consumption and update rate.
ESP32:    Current value: 00.80 m
ESP32: U: Change the update rate. Affects power consumption.
ESP32:    Current value: 10.0 Hz
ESP32: L: Change the maximum step length of the measurements. Affects power consumption, update rate, and resolution.
ESP32:    Current value: 04 (10.0 mm)
ESP32: P: Change the maximum measurement profile. Affects power consumption, update rate, and accuracy.
ESP32:    Current value: 3
ESP32: Q: Change the signal quality. Affects power consumption, update rate, and accuracy.
ESP32:    Current value: 20.0
ESP32: R: Change the reflector shape.
ESP32:    Current value: 1 (0: generic, 1: planar)
ESP32: T: Change the threshold sensitivity. Affects accuracy.
ESP32:    Current value: 0.50
ESP32: W: Set the text width for the Bluetooth UART output.
ESP32:    Current value: 040 characters
ESP32: A: Measure the actual update rate.
ESP32:    True update rate: 09.9 Hz
ESP32: B: Print to Bluetooth in serial plotter mode for two minutes.
ESP32:    Useful for tuning settings with visual indicators.
ESP32:    Recommended to use Arduino IDE serial plotter.
ESP32: X: Exit the menu.
ESP32: 
Input: w
ESP32: 
ESP32: Set the text width for the Bluetooth UART output. Current value: 040 characters
ESP32: Format: XXX
ESP32:  Input must match format exactly. Enter a single integer between 010 and 140, inclusive.
ESP32:  Alternatively, enter "000" to disable text wrapping.
ESP32: Notes:
ESP32:  The text in the Bluetooth terminal can be adjusted for the width of your device.
ESP32: Example:
ESP32:  The user is interfacing with the ESP32 using a mobile phone Bluetooth serial terminal.
ESP32:  The user notices that the text does not wrap around the phone screen properly, with five characters hanging at the end of each line.
ESP32:  User would subtract 5 from the current text width and enter the result into the terminal.
ESP32: 
Input: 041
ESP32: 
ESP32: Text width set to 041 characters
ESP32: Is this the desired value? Type Y for yes, any other character for no.
ESP32: 
Input: y
ESP32: 
ESP32: Value saved.
ESP32: 
ESP32: --- CONFIGURATION MENU ---
ESP32: Send one of the below characters to change that configuration setting.
ESP32: Changes will be saved upon exiting menu.
ESP32: S: Change the start of the measurement range. Affects power consumption and update rate.
ESP32:    Current value: 00.20 m
ESP32: E: Change the end of the measurement range. Affects power consumption and update rate.
ESP32:    Current value: 00.80 m
ESP32: U: Change the update rate. Affects power consumption.
ESP32:    Current value: 10.0 Hz
ESP32: L: Change the maximum step length of the measurements. Affects power consumption, update rate, and resolution.
ESP32:    Current value: 04 (10.0 mm)
ESP32: P: Change the maximum measurement profile. Affects power consumption, update rate, and accuracy.
ESP32:    Current value: 3
ESP32: Q: Change the signal quality. Affects power consumption, update rate, and accuracy.
ESP32:    Current value: 20.0
ESP32: R: Change the reflector shape.
ESP32:    Current value: 1 (0: generic, 1: planar)
ESP32: T: Change the threshold sensitivity. Affects accuracy.
ESP32:    Current value: 0.50
ESP32: W: Set the text width for the Bluetooth UART output.
ESP32:    Current value: 041 characters
ESP32: A: Measure the actual update rate.
ESP32:    True update rate: 09.9 Hz
ESP32: B: Print to Bluetooth in serial plotter mode for two minutes.
ESP32:    Useful for tuning settings with visual indicators.
ESP32:    Recommended to use Arduino IDE serial plotter.
ESP32: X: Exit the menu.
ESP32: 
Input: x
ESP32: 
ESP32: Send any character to re-open configuration menu.
ESP32: 
ESP32: New config file saved
ESP32: Configuration saved to SD card. Returning to normal operations.
ESP32: 
ESP32: Sending config to STM...
ESP32: Sent from ESP32:     00.20,00.80,10.0,04,3,20.0,1,0.50,0,09.9
ESP32: Received from STM32: M807
ESP32: Received from STM32: M807
ESP32: Received from STM32: M807
ESP32: Received from STM32: M807
ESP32: Received from STM32: M807
ESP32: Received from STM32: M807
ESP32: Received from STM32: M807
ESP32: Received from STM32: 00.20,00.80,10.0,04,3,20.0,1,0.50,0,09.9
ESP32: Received from STM32: M808
STM32: Configuration received and loaded onto radar sensor.
STM32: 
STM32: 00:01:56.065 (I) (detector_distance) Detector Distance Config
STM32: 00:01:56.065 (I) (detector_distance) start_m: 0.200000
STM32: 00:01:56.066 (I) (detector_distance) end_m: 0.800000
STM32: 00:01:56.067 (I) (detector_distance) max_step_length: 4
STM32: 00:01:56.068 (I) (detector_distance) max_profile: PROFILE_3
STM32: 00:01:56.069 (I) (detector_distance) close_range_leakage_cancellation: false
STM32: 00:01:56.070 (I) (detector_distance) signal_quality: 20.000000
STM32: 00:01:56.071 (I) (detector_distance) threshold_method: C00:01:56.076 (00:01:56.077 (I) (detector_distance) Offset Ca00:01:56.08
STM32: 2 (I) (config) inter_sweep_idle_state: READY
STM32: 00:01:56.083 (I) (con00:01:56.090 (I) (config)     enable_loopback  : true
STM32: 00:01:56.00:01:56.096 (I) (config) double_buffering: false
STM32: 00:01:56.097 (I) (config) inter_frame_idle_state: DEEP_SLEEP
STM32: 00:01:56.098 (I)00:01:56.107 (I) (detector_di00:01:56.108 (I)00:01:56.112 (I) (con00:01:56.113 (I) (config) inter_sweep_idle_st
STM32: ate: READ00:01:56.119 (I) (config)     phase_enhancement: true
STM32: 00:01
STM32: M114

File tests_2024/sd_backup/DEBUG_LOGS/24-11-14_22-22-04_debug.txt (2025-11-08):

ESP32: Loaded config file.
ESP32: Configuration loaded from SD card.
ESP32: Loaded previous GPS coordinates: 38°05'04.69"N 122°34'16.59"W
STM32: M807
ESP32: Sending config to STM...
ESP32: Sent from ESP32:     00.20,00.80,10.0,04,3,20.0,1,0.50,0,09.9
ESP32: Received from STM32: M807
ESP32: Received from STM32: M807
ESP32: Received from STM32: M807
ESP32: Received from STM32: 00.20,00.80,10.0,04,3,20.0,1,0.50,0,09.9
ESP32: Received from STM32: M808
STM32: Configuration received and loaded onto radar sensor.
STM32: 
STM32: 00:00:07.383 (I) (detector_distance) Detector Distance Config
STM32: 00:00:07.383 (I) (detector_distance) start_m: 0.200000
STM32: 00:00:07.384 (I) (detector_distance) end_m: 0.800000
STM32: 00:00:07.385 (I) (detector_distance) max_step_length: 4
STM32: 00:00:07.386 (I) (detector_distance) max_profile: PROFILE_3
STM32: 00:00:07.387 (I) (detector_distance) close_range_leakage_cancellation: false
STM32: 00:00:07.388 (I) (detector_distance) signal_quality: 20.000000
STM32: 00:00:07.389 (I) (detector_distance) threshold_method: C00:00:07.394 00:00:07.395 (I) (detector_distance) Offset Cal00:00:07.40
STM32: 0 (I) (config) inter_sweep_idle_state: READY
STM32: 00:00:07.401 (I) (con00:00:07.408 (I) (config)     enable_loopback  : true
STM32: 00:00:07.00:00:07.414 (I) (config) double_buffering: false
STM32: 00:00:07.415 (I) (config) inter_frame_idle_state: DEEP_SLEEP
STM32: 00:00:07.416 (I)00:00:07.425 (I) (detector_00:00:07.426 (I) (00:00:07.430 (I00:00:07.431 (I) (config) inter_sweep_idle_state: R
STM32: EADY
STM32: 00:000:00:07.437 (I) (config)     phase_enhancement: true
STM32: 00:00
STM32: M114
STM32: DATA_START
ESP32: ---------- ---------- ---------- ---------- -------- ---------- ---------- ---------- ----------
ESP32: ---------- ---------- ---------- ---------- NEW DATA ---------- ---------- ---------- ----------
ESP32: ---------- ---------- ---------- ---------- -------- ---------- ---------- ---------- ----------
ESP32: First Data File Since Powering On: True
ESP32: Data File: /DATA/24-11-14_22-22-12_data.txt
ESP32: Start Time: [24/11/14 22:22:12.892]
ESP32: Location: 38°05'04.69"N 122°34'16.59"W
ESP32: Elevation: 54.8
ESP32: Start of range: 0.20 m
ESP32: End of range: 0.80 m
ESP32: Update rate: 10.0 Hz
ESP32: Maximum step length: 4 (10.0 mm)
ESP32: Maximum profile: 3
ESP32: Signal quality: 20.0
ESP32: Reflector shape: 1 (0: generic, 1: planar)
ESP32: Threshold sensitivity: 0.50
ESP32: True update rate: 9.9 Hz
ESP32: Text width: 41 characters
ESP32: ---
ESP32: Time: 22:23:01 PST
ESP32: Location: 38°05'05.12"N 122°34'16.17"W
ESP32: Elevation: 53.6 m
ESP32: New config file saved
ESP32: GPS POWEROFF
ESP32: GPS POWERON
ESP32: Time: 23:22:17 PST
ESP32: Location: 38°05'05.05"N 122°34'16.39"W
ESP32: Elevation: 50.9 m
ESP32: New config file saved
ESP32: GPS POWEROFF
STM32: M19
STM32: M19
STM32: M11
STM32: M19
ESP32: GPS POWERON
ESP32: Time: 00:22:43 PST
ESP32: Location: 38°05'05.06"N 122°34'16.06"W
ESP32: Elevation: 31.4 m
ESP32: New config file saved
ESP32: GPS POWEROFF
ESP32: RTC synchronized with GPS time:
ESP32: Old RTC time: 24/11/15 00:22:44
ESP32: New RTC time: 24/11/15 00:22:43
STM32: 
STM32: M1
ESP32: GPS POWERON
ESP32: Time: 01:22:16 PST
ESP32: Location: 38°05'05.20"N 122°34'16.28"W
ESP32: Elevation: 32.7 m
ESP32: New config file saved
ESP32: GPS POWEROFF
STM32: 
STM32: M19
STM32: b
ESP32: GPS POWERON
ESP32: Time: 02:22:34 PST
ESP32: Location: 38°05'05.23"N 122°34'16.12"W
ESP32: Elevation: 35.0 m
ESP32: New config file saved
ESP32: GPS POWEROFF
STM32: 
STM32: M1
STM32: M
STM32: M19
STM32: M1
ESP32: GPS POWERON
ESP32: Time: 03:22:21 PST
ESP32: Location: 38°05'06.79"N 122°34'15.93"W
ESP32: Elevation: 53.5 m
ESP32: New config file saved
ESP32: GPS POWEROFF
ESP32: RTC synchronized with GPS time:
ESP32: Old RTC time: 24/11/15 03:22:22
ESP32: New RTC time: 24/11/15 03:22:21
STM32: M19
STM32: M19
STM32: M����2
STM32: M1
STM32: 
STM32: M1
STM32: M1
ESP32: GPS POWERON
ESP32: Time: 04:22:43 PST
ESP32: Location: 38°05'04.95"N 122°34'16.28"W
ESP32: Elevation: 36.4 m
ESP32: New config file saved
ESP32: GPS POWEROFF
STM32: M1
STM32: M19
STM32: 
STM32: M19
STM32: M1
STM32: M
STM32: 
ESP32: GPS POWERON
ESP32: Time: 05:22:17 PST
ESP32: Location: 38°05'05.46"N 122°34'16.39"W
ESP32: Elevation: 48.4 m
ESP32: New config file saved
ESP32: GPS POWEROFF
ESP32: RTC synchronized with GPS time:
ESP32: Old RTC time: 24/11/15 05:22:18
ESP32: New RTC time: 24/11/15 05:22:17
STM32: M19
STM32: M19
STM32: 
STM32: M1
STM32: M19
STM32: 
STM32: 
ESP32: GPS POWERON
ESP32: Time: 06:22:25 PST
ESP32: Location: 38°05'05.12"N 122°34'16.34"W
ESP32: Elevation: 57.5 m
ESP32: New config file saved
ESP32: GPS POWEROFF
STM32: M
STM32: M1
STM32: M
STM32: M1
STM32: 
STM32: M19
STM32: M
STM32: M19
STM32: M
STM32: 
ESP32: GPS POWERON
ESP32: Time: 07:22:43 PST
ESP32: Location: 38°05'05.10"N 122°34'16.28"W
ESP32: Elevation: 38.4 m
ESP32: New config file saved
ESP32: GPS POWEROFF
ESP32: RTC synchronized with GPS time:
ESP32: Old RTC time: 24/11/15 07:22:44
ESP32: New RTC time: 24/11/15 07:22:43
STM32: �|���	�����
�h����
STM32: M1
STM32: M1
STM32: M19
STM32: M
STM32: M19
ESP32: GPS POWERON
ESP32: Time: 08:22:18 PST
ESP32: Location: 38°05'05.16"N 122°34'16.23"W
ESP32: Elevation: 50.3 m
ESP32: New config file saved
ESP32: GPS POWEROFF
STM32: M1
STM32: M1
STM32: M
STM32: M1
STM32: 
STM32: M19
STM32: M1
STM32: M

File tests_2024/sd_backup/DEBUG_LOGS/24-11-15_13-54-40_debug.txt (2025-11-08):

ESP32: Loaded config file.
ESP32: Configuration loaded from SD card.
ESP32: Loaded previous GPS coordinates: 38°05'05.16"N 122°34'16.23"W
STM32: M807
ESP32: Sending config to STM...
ESP32: Sent from ESP32:     00.20,00.80,10.0,04,3,20.0,1,0.50,0,09.9
ESP32: Received from STM32: M807
ESP32: Received from STM32: M807
ESP32: Received from STM32: M807
ESP32: Received from STM32: 00.20,00.80,10.0,04,3,20.0,1,0.50,0,09.9
ESP32: Received from STM32: M808
STM32: Configuration received and loaded onto radar sensor.
STM32: 
STM32: 00:00:07.378 (I) (detector_distance) Detector Distance Config
STM32: 00:00:07.378 (I) (detector_distance) start_m: 0.200000
STM32: 00:00:07.379 (I) (detector_distance) end_m: 0.800000
STM32: 00:00:07.380 (I) (detector_distance) max_step_length: 4
STM32: 00:00:07.381 (I) (detector_distance) max_profile: PROFILE_3
STM32: 00:00:07.382 (I) (detector_distance) close_range_leakage_cancellation: false
STM32: 00:00:07.383 (I) (detector_distance) signal_quality: 20.000000
STM32: 00:00:07.384 (I) (detector_distance) threshold_method: C00:00:07.389 (I)00:00:07.390 (I) (detector_distance) Offset 00:00:07.39
STM32: 5 (I) (config) inter_sweep_idle_state: READY
STM32: 00:00:07.396 (I) (con00:00:07.403 (I) (config)     enable_loopback  : true
STM32: 00:00:07.00:00:07.409 (I) (config) double_buffering: false
STM32: 00:00:07.410 (I) (config) inter_frame_idle_state: DEEP_SLEEP
STM32: 00:00:07.411 (I)00:00:07.420 (I) (detector_distanc00:00:07.4200:00:07.425 (I) (confi00:00:07.426 (I) (config) inter_sweep_idle_
STM32: state: RE00:00:07.432 (I) (config)     phase_enhancement: true
STM32: 00:00
STM32: M114
STM32: DATA_START
ESP32: ---------- ---------- ---------- ---------- -------- ---------- ---------- ---------- ----------
ESP32: ---------- ---------- ---------- ---------- NEW DATA ---------- ---------- ---------- ----------
ESP32: ---------- ---------- ---------- ---------- -------- ---------- ---------- ---------- ----------
ESP32: First Data File Since Powering On: True
ESP32: Data File: /DATA/24-11-15_13-54-49_data.txt
ESP32: Start Time: [24/11/15 13:54:49.892]
ESP32: Location: 38°05'05.16"N 122°34'16.23"W
ESP32: Elevation: 50.3
ESP32: Start of range: 0.20 m
ESP32: End of range: 0.80 m
ESP32: Update rate: 10.0 Hz
ESP32: Maximum step length: 4 (10.0 mm)
ESP32: Maximum profile: 3
ESP32: Signal quality: 20.0
ESP32: Reflector shape: 1 (0: generic, 1: planar)
ESP32: Threshold sensitivity: 0.50
ESP32: True update rate: 9.9 Hz
ESP32: Text width: 41 characters
ESP32: ---
STM32: 
STM32: Stopping radar...
STM32: Process will take approximately 1.3 seconds.
STM32: 
STM32: Radar stopped.
STM32: 
ESP32: --- CONFIGURATION MENU ---
ESP32: Send one of the below characters to change that configuration setting.
ESP32: Changes will be saved upon exiting menu.
ESP32: S: Change the start of the measurement range. Affects power consumption and update rate.
ESP32:    Current value: 00.20 m
ESP32: E: Change the end of the measurement range. Affects power consumption and update rate.
ESP32:    Current value: 00.80 m
ESP32: U: Change the update rate. Affects power consumption.
ESP32:    Current value: 10.0 Hz
ESP32: L: Change the maximum step length of the measurements. Affects power consumption, update rate, and resolution.
ESP32:    Current value: 04 (10.0 mm)
ESP32: P: Change the maximum measurement profile. Affects power consumption, update rate, and accuracy.
ESP32:    Current value: 3
ESP32: Q: Change the signal quality. Affects power consumption, update rate, and accuracy.
ESP32:    Current value: 20.0
ESP32: R: Change the reflector shape.
ESP32:    Current value: 1 (0: generic, 1: planar)
ESP32: T: Change the threshold sensitivity. Affects accuracy.
ESP32:    Current value: 0.50
ESP32: W: Set the text width for the Bluetooth UART output.
ESP32:    Current value: 041 characters
ESP32: A: Measure the actual update rate.
ESP32:    True update rate: 09.9 Hz
ESP32: B: Print to Bluetooth in serial plotter mode for two minutes.
ESP32:    Useful for tuning settings with visual indicators.
ESP32:    Recommended to use Arduino IDE serial plotter.
ESP32: X: Exit the menu.
ESP32: 
Input: s
ESP32: 
ESP32: Set the start of the measurement range. Current value: 00.20 m
ESP32: Format: XX.XX
ESP32:  Input must match format exactly. Enter leading and trailing zeros as appropriate.
ESP32:  Value must be between 00.10 and 20.00, inclusive.
ESP32:  Units are in meters.
ESP32: Notes:
ESP32:  Generally advised to leave a margin of 0.1m above maximum wave height.
ESP32:  Keep as high as possible. Greatly affects power consumption and maximum possible update rate.
ESP32: Example:
ESP32:  Radar is placed 10m above average wave height, and waves height fluctuates within +/- 1m.
ESP32:  Start of measurement range should be set to 0.8m.
ESP32:  User would enter "00.80" into terminal with no quotes.
ESP32: 
Input: 01.00
ESP32: 
ESP32: Start of measurement range set to 01.00 m
ESP32: Is this the desired value? Type Y for yes, any other character for no.
ESP32: 
Input: y
ESP32: 
ESP32: Value saved.
ESP32: 
ESP32: --- CONFIGURATION MENU ---
ESP32: Send one of the below characters to change that configuration setting.
ESP32: Changes will be saved upon exiting menu.
ESP32: S: Change the start of the measurement range. Affects power consumption and update rate.
ESP32:    Current value: 01.00 m
ESP32: E: Change the end of the measurement range. Affects power consumption and update rate.
ESP32:    Current value: 00.80 m
ESP32: U: Change the update rate. Affects power consumption.
ESP32:    Current value: 10.0 Hz
ESP32: L: Change the maximum step length of the measurements. Affects power consumption, update rate, and resolution.
ESP32:    Current value: 04 (10.0 mm)
ESP32: P: Change the maximum measurement profile. Affects power consumption, update rate, and accuracy.
ESP32:    Current value: 3
ESP32: Q: Change the signal quality. Affects power consumption, update rate, and accuracy.
ESP32:    Current value: 20.0
ESP32: R: Change the reflector shape.
ESP32:    Current value: 1 (0: generic, 1: planar)
ESP32: T: Change the threshold sensitivity. Affects accuracy.
ESP32:    Current value: 0.50
ESP32: W: Set the text width for the Bluetooth UART output.
ESP32:    Current value: 041 characters
ESP32: A: Measure the actual update rate.
ESP32:    True update rate: 09.9 Hz
ESP32: B: Print to Bluetooth in serial plotter mode for two minutes.
ESP32:    Useful for tuning settings with visual indicators.
ESP32:    Recommended to use Arduino IDE serial plotter.
ESP32: X: Exit the menu.
ESP32: 
Input: e
ESP32: 
ESP32: Set the end of the measurement range. Current value: 00.80 m
ESP32: Format: XX.XX
ESP32:  Input must match format exactly. Enter leading and trailing zeros as appropriate.
ESP32:  Value must be between 00.10 and 20.00, inclusive.
ESP32:  Units are in meters.
ESP32: Notes:
ESP32:  Generally advised to leave a margin of 0.1m below maximum wave height.
ESP32:  Keep as low as possible. Greatly affects power consumption and maximum possible update rate.
ESP32: Example:
ESP32:  Radar is placed 10m above average wave height, and waves height fluctuates within +/- 1m.
ESP32:  End of measurement range should be set to 1.2m.
ESP32:  User would enter "01.20" into terminal with no quotes.
ESP32: 
Input: 05.00
ESP32: 
ESP32: End of measurement range set to 05.00 m
ESP32: Is this the desired value? Type Y for yes, any other character for no.
ESP32: 
Input: y
ESP32: 
ESP32: Value saved.
ESP32: 
ESP32: --- CONFIGURATION MENU ---
ESP32: Send one of the below characters to change that configuration setting.
ESP32: Changes will be saved upon exiting menu.
ESP32: S: Change the start of the measurement range. Affects power consumption and update rate.
ESP32:    Current value: 01.00 m
ESP32: E: Change the end of the measurement range. Affects power consumption and update rate.
ESP32:    Current value: 05.00 m
ESP32: U: Change the update rate. Affects power consumption.
ESP32:    Current value: 10.0 Hz
ESP32: L: Change the maximum step length of the measurements. Affects power consumption, update rate, and resolution.
ESP32:    Current value: 04 (10.0 mm)
ESP32: P: Change the maximum measurement profile. Affects power consumption, update rate, and accuracy.
ESP32:    Current value: 3
ESP32: Q: Change the signal quality. Affects power consumption, update rate, and accuracy.
ESP32:    Current value: 20.0
ESP32: R: Change the reflector shape.
ESP32:    Current value: 1 (0: generic, 1: planar)
ESP32: T: Change the threshold sensitivity. Affects accuracy.
ESP32:    Current value: 0.50
ESP32: W: Set the text width for the Bluetooth UART output.
ESP32:    Current value: 041 characters
ESP32: A: Measure the actual update rate.
ESP32:    True update rate: 09.9 Hz
ESP32: B: Print to Bluetooth in serial plotter mode for two minutes.
ESP32:    Useful for tuning settings with visual indicators.
ESP32:    Recommended to use Arduino IDE serial plotter.
ESP32: X: Exit the menu.
ESP32: 
Input: x
ESP32: 
ESP32: Send any character to re-open configuration menu.
ESP32: 
ESP32: New config file saved
ESP32: Configuration saved to SD card. Returning to normal operations.
ESP32: 
ESP32: Sending config to STM...
ESP32: Sent from ESP32:     01.00,05.00,10.0,04,3,20.0,1,0.50,0,09.9
ESP32: Received from STM32: M807
ESP32: Received from STM32: M807
ESP32: Received from STM32: M807
ESP32: Received from STM32: M807
ESP32: Received from STM32: M807
ESP32: Received from STM32: M807
ESP32: Received from STM32: 01.00,05.00,10.0,04,3,20.0,1,0.50,0,09.9
ESP32: Received from STM32: M808
STM32: Configuration received and loaded onto radar sensor.
STM32: 
ESP32: Time: 13:56:37 PST
ESP32: Location: 36°48'09.25"N 121°47'12.36"W
ESP32: Elevation: 12.4 m
ESP32: New config file saved
ESP32: GPS POWEROFF
ESP32: RTC synchronized with GPS time:
ESP32: Old RTC time: 24/11/15 13:56:39
ESP32: New RTC time: 24/11/15 13:56:37
STM32: M114
STM32: DATA_START
ESP32: ---------- ---------- ---------- ---------- -------- ---------- ---------- ---------- ----------
ESP32: ---------- ---------- ---------- ---------- NEW DATA ---------- ---------- ---------- ----------
ESP32: ---------- ---------- ---------- ---------- -------- ---------- ---------- ---------- ----------
ESP32: First Data File Since Powering On: False
ESP32: Data File: /DATA/24-11-15_13-56-37_data.txt
ESP32: Start Time: [24/11/15 13:56:40.388]
ESP32: Location: 36°48'09.25"N 121°47'12.36"W
ESP32: Elevation: 12.4 m
ESP32: Start of range: 1.00 m
ESP32: End of range: 5.00 m
ESP32: Update rate: 10.0 Hz
ESP32: Maximum step length: 4 (10.0 mm)
ESP32: Maximum profile: 3
ESP32: Signal quality: 20.0
ESP32: Reflector shape: 1 (0: generic, 1: planar)
ESP32: Threshold sensitivity: 0.50
ESP32: True update rate: 9.9 Hz
ESP32: Text width: 41 characters
ESP32: ---
STM32: M
STM32: 
STM32: Stopping radar...
STM32: Process will take approximately 1.3 seconds.
STM32: 
STM32: Radar stopped.
STM32: 
ESP32: --- CONFIGURATION MENU ---
ESP32: Send one of the below characters to change that configuration setting.
ESP32: Changes will be saved upon exiting menu.
ESP32: S: Change the start of the measurement range. Affects power consumption and update rate.
ESP32:    Current value: 01.00 m
ESP32: E: Change the end of the measurement range. Affects power consumption and update rate.
ESP32:    Current value: 05.00 m
ESP32: U: Change the update rate. Affects power consumption.
ESP32:    Current value: 10.0 Hz
ESP32: L: Change the maximum step length of the measurements. Affects power consumption, update rate, and resolution.
ESP32:    Current value: 04 (10.0 mm)
ESP32: P: Change the maximum measurement profile. Affects power consumption, update rate, and accuracy.
ESP32:    Current value: 3
ESP32: Q: Change the signal quality. Affects power consumption, update rate, and accuracy.
ESP32:    Current value: 20.0
ESP32: R: Change the reflector shape.
ESP32:    Current value: 1 (0: generic, 1: planar)
ESP32: T: Change the threshold sensitivity. Affects accuracy.
ESP32:    Current value: 0.50
ESP32: W: Set the text width for the Bluetooth UART output.
ESP32:    Current value: 041 characters
ESP32: A: Measure the actual update rate.
ESP32:    True update rate: 09.9 Hz
ESP32: B: Print to Bluetooth in serial plotter mode for two minutes.
ESP32:    Useful for tuning settings with visual indicators.
ESP32:    Recommended to use Arduino IDE serial plotter.
ESP32: X: Exit the menu.
ESP32: 
Input: s
ESP32: 
ESP32: Set the start of the measurement range. Current value: 01.00 m
ESP32: Format: XX.XX
ESP32:  Input must match format exactly. Enter leading and trailing zeros as appropriate.
ESP32:  Value must be between 00.10 and 20.00, inclusive.
ESP32:  Units are in meters.
ESP32: Notes:
ESP32:  Generally advised to leave a margin of 0.1m above maximum wave height.
ESP32:  Keep as high as possible. Greatly affects power consumption and maximum possible update rate.
ESP32: Example:
ESP32:  Radar is placed 10m above average wave height, and waves height fluctuates within +/- 1m.
ESP32:  Start of measurement range should be set to 0.8m.
ESP32:  User would enter "00.80" into terminal with no quotes.
ESP32: 
Input: 00.50
ESP32: 
ESP32: Start of measurement range set to 00.50 m
ESP32: Is this the desired value? Type Y for yes, any other character for no.
ESP32: 
Input: y
ESP32: 
ESP32: Value saved.
ESP32: 
ESP32: --- CONFIGURATION MENU ---
ESP32: Send one of the below characters to change that configuration setting.
ESP32: Changes will be saved upon exiting menu.
ESP32: S: Change the start of the measurement range. Affects power consumption and update rate.
ESP32:    Current value: 00.50 m
ESP32: E: Change the end of the measurement range. Affects power consumption and update rate.
ESP32:    Current value: 05.00 m
ESP32: U: Change the update rate. Affects power consumption.
ESP32:    Current value: 10.0 Hz
ESP32: L: Change the maximum step length of the measurements. Affects power consumption, update rate, and resolution.
ESP32:    Current value: 04 (10.0 mm)
ESP32: P: Change the maximum measurement profile. Affects power consumption, update rate, and accuracy.
ESP32:    Current value: 3
ESP32: Q: Change the signal quality. Affects power consumption, update rate, and accuracy.
ESP32:    Current value: 20.0
ESP32: R: Change the reflector shape.
ESP32:    Current value: 1 (0: generic, 1: planar)
ESP32: T: Change the threshold sensitivity. Affects accuracy.
ESP32:    Current value: 0.50
ESP32: W: Set the text width for the Bluetooth UART output.
ESP32:    Current value: 041 characters
ESP32: A: Measure the actual update rate.
ESP32:    True update rate: 09.9 Hz
ESP32: B: Print to Bluetooth in serial plotter mode for two minutes.
ESP32:    Useful for tuning settings with visual indicators.
ESP32:    Recommended to use Arduino IDE serial plotter.
ESP32: X: Exit the menu.
ESP32: 
Input: e
ESP32: 
ESP32: Set the end of the measurement range. Current value: 05.00 m
ESP32: Format: XX.XX
ESP32:  Input must match format exactly. Enter leading and trailing zeros as appropriate.
ESP32:  Value must be between 00.10 and 20.00, inclusive.
ESP32:  Units are in meters.
ESP32: Notes:
ESP32:  Generally advised to leave a margin of 0.1m below maximum wave height.
ESP32:  Keep as low as possible. Greatly affects power consumption and maximum possible update rate.
ESP32: Example:
ESP32:  Radar is placed 10m above average wave height, and waves height fluctuates within +/- 1m.
ESP32:  End of measurement range should be set to 1.2m.
ESP32:  User would enter "01.20" into terminal with no quotes.
ESP32: 
Input: 04.50
ESP32: 
ESP32: End of measurement range set to 04.50 m
ESP32: Is this the desired value? Type Y for yes, any other character for no.
ESP32: 
Input: y
ESP32: 
ESP32: Value saved.
ESP32: 
ESP32: --- CONFIGURATION MENU ---
ESP32: Send one of the below characters to change that configuration setting.
ESP32: Changes will be saved upon exiting menu.
ESP32: S: Change the start of the measurement range. Affects power consumption and update rate.
ESP32:    Current value: 00.50 m
ESP32: E: Change the end of the measurement range. Affects power consumption and update rate.
ESP32:    Current value: 04.50 m
ESP32: U: Change the update rate. Affects power consumption.
ESP32:    Current value: 10.0 Hz
ESP32: L: Change the maximum step length of the measurements. Affects power consumption, update rate, and resolution.
ESP32:    Current value: 04 (10.0 mm)
ESP32: P: Change the maximum measurement profile. Affects power consumption, update rate, and accuracy.
ESP32:    Current value: 3
ESP32: Q: Change the signal quality. Affects power consumption, update rate, and accuracy.
ESP32:    Current value: 20.0
ESP32: R: Change the reflector shape.
ESP32:    Current value: 1 (0: generic, 1: planar)
ESP32: T: Change the threshold sensitivity. Affects accuracy.
ESP32:    Current value: 0.50
ESP32: W: Set the text width for the Bluetooth UART output.
ESP32:    Current value: 041 characters
ESP32: A: Measure the actual update rate.
ESP32:    True update rate: 09.9 Hz
ESP32: B: Print to Bluetooth in serial plotter mode for two minutes.
ESP32:    Useful for tuning settings with visual indicators.
ESP32:    Recommended to use Arduino IDE serial plotter.
ESP32: X: Exit the menu.
ESP32: 
Input: q
ESP32: 
ESP32: Set the signal quality. Current value: 20.0
ESP32: Format: XX.X
ESP32:  Input must match format exactly. Enter leading and trailing zeros as appropriate.
ESP32:  Value must be between 00.0 and 35.0, inclusive.
ESP32:  Units are arbitrary.
ESP32: Notes:
ESP32:  Higher signal quality results in a higher signal-to-noise ratio target, and increases the number of averages
ESP32:  taken for a single datapoint. This generally increases the accuracy of measurements.
ESP32:  Keep as low as possible. Affects power consumption and maximum possible update rate.
ESP32: Example:
ESP32:  The user starts the radar with signal quality setting of 15.0, but measurements appear inaccurate.
ESP32:  The user should increase the profile setting by 1.0, repeating until the measurements are accurate enough.
ESP32:  User would enter "16.0" into terminal with no quotes.
ESP32: 
Input: 35.0
ESP32: 
ESP32: Signal quality set to 35.0
ESP32: Is this the desired value? Type Y for yes, any other character for no.
ESP32: 
Input: y
ESP32: 
ESP32: Value saved.
ESP32:
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

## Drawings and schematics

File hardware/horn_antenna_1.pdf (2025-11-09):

50.8 ± 1
25.4 ± 1

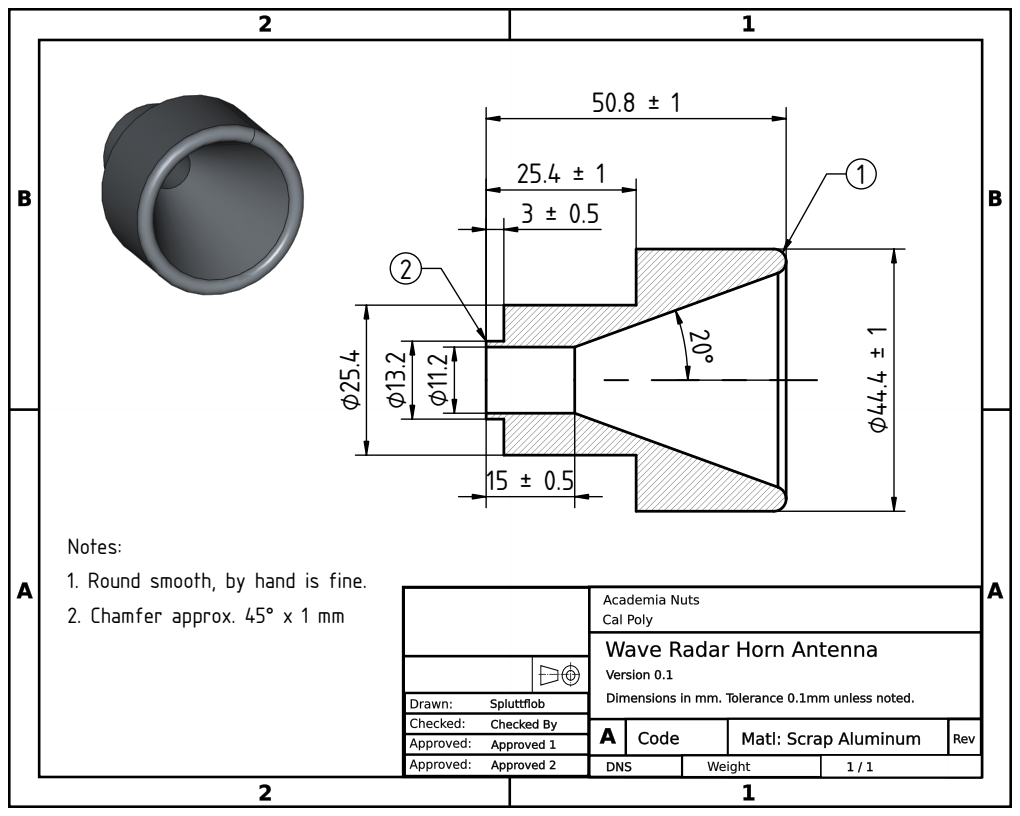
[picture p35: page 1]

Notes:
1. Round smooth, by hand is fine.
2. Chamfer approx. 45° x 1 mm

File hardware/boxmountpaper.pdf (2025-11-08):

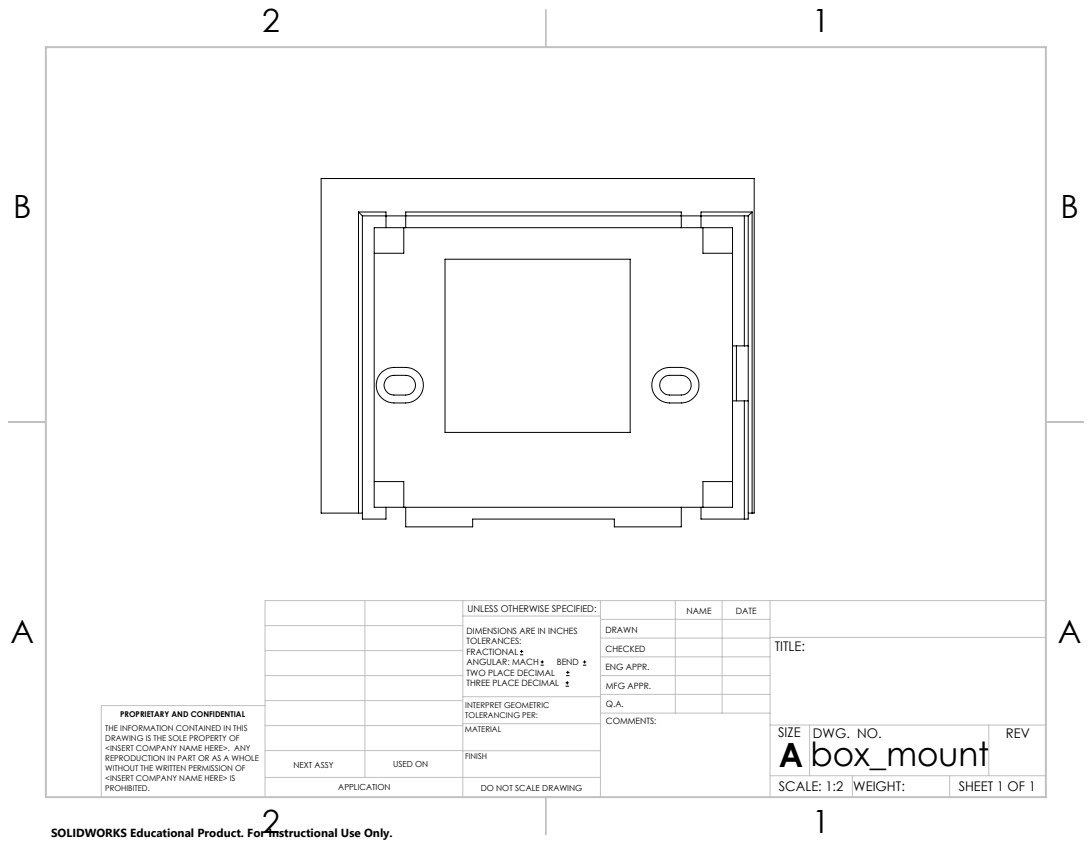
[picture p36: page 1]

UNLESS OTHERWISE SPECIFIED: | | NAME | DATE
DIMENSIONS ARE IN INCHES TOLERANCES: FRACTIONAL ANGULAR: MACH BEND TWO PLACE DECIMAL THREE PLACE DECIMAL | DRAWN

CHECKED | | | TITLE:

ENG APPR.
MFG APPR.

INTERPRET GEOMETRIC TOLERANCING PER: | Q.A.
MATERIAL | | SIZE A | DWG. NO. box_mount | REV

PROPRIETARY AND CONFIDENTIAL
THE INFORMATION CONTAINED IN THIS
DRAWING IS THE SOLE PROPERTY OF
<INSERT COMPANY NAME HERE>. ANY
REPRODUCTION IN PART OR AS A WHOLE
WITHOUT THE WRITTEN PERMISSION OF
<INSERT COMPANY NAME HERE> IS
PROHIBITED.

NEXT ASSY | USED ON | FINISH

APPLICATION | DO NOT SCALE DRAWING | | SCALE: 1:2 | WEIGHT: | SHEET 1 OF 1

SOLIDWORKS Educational Product. For Instructional Use Only.

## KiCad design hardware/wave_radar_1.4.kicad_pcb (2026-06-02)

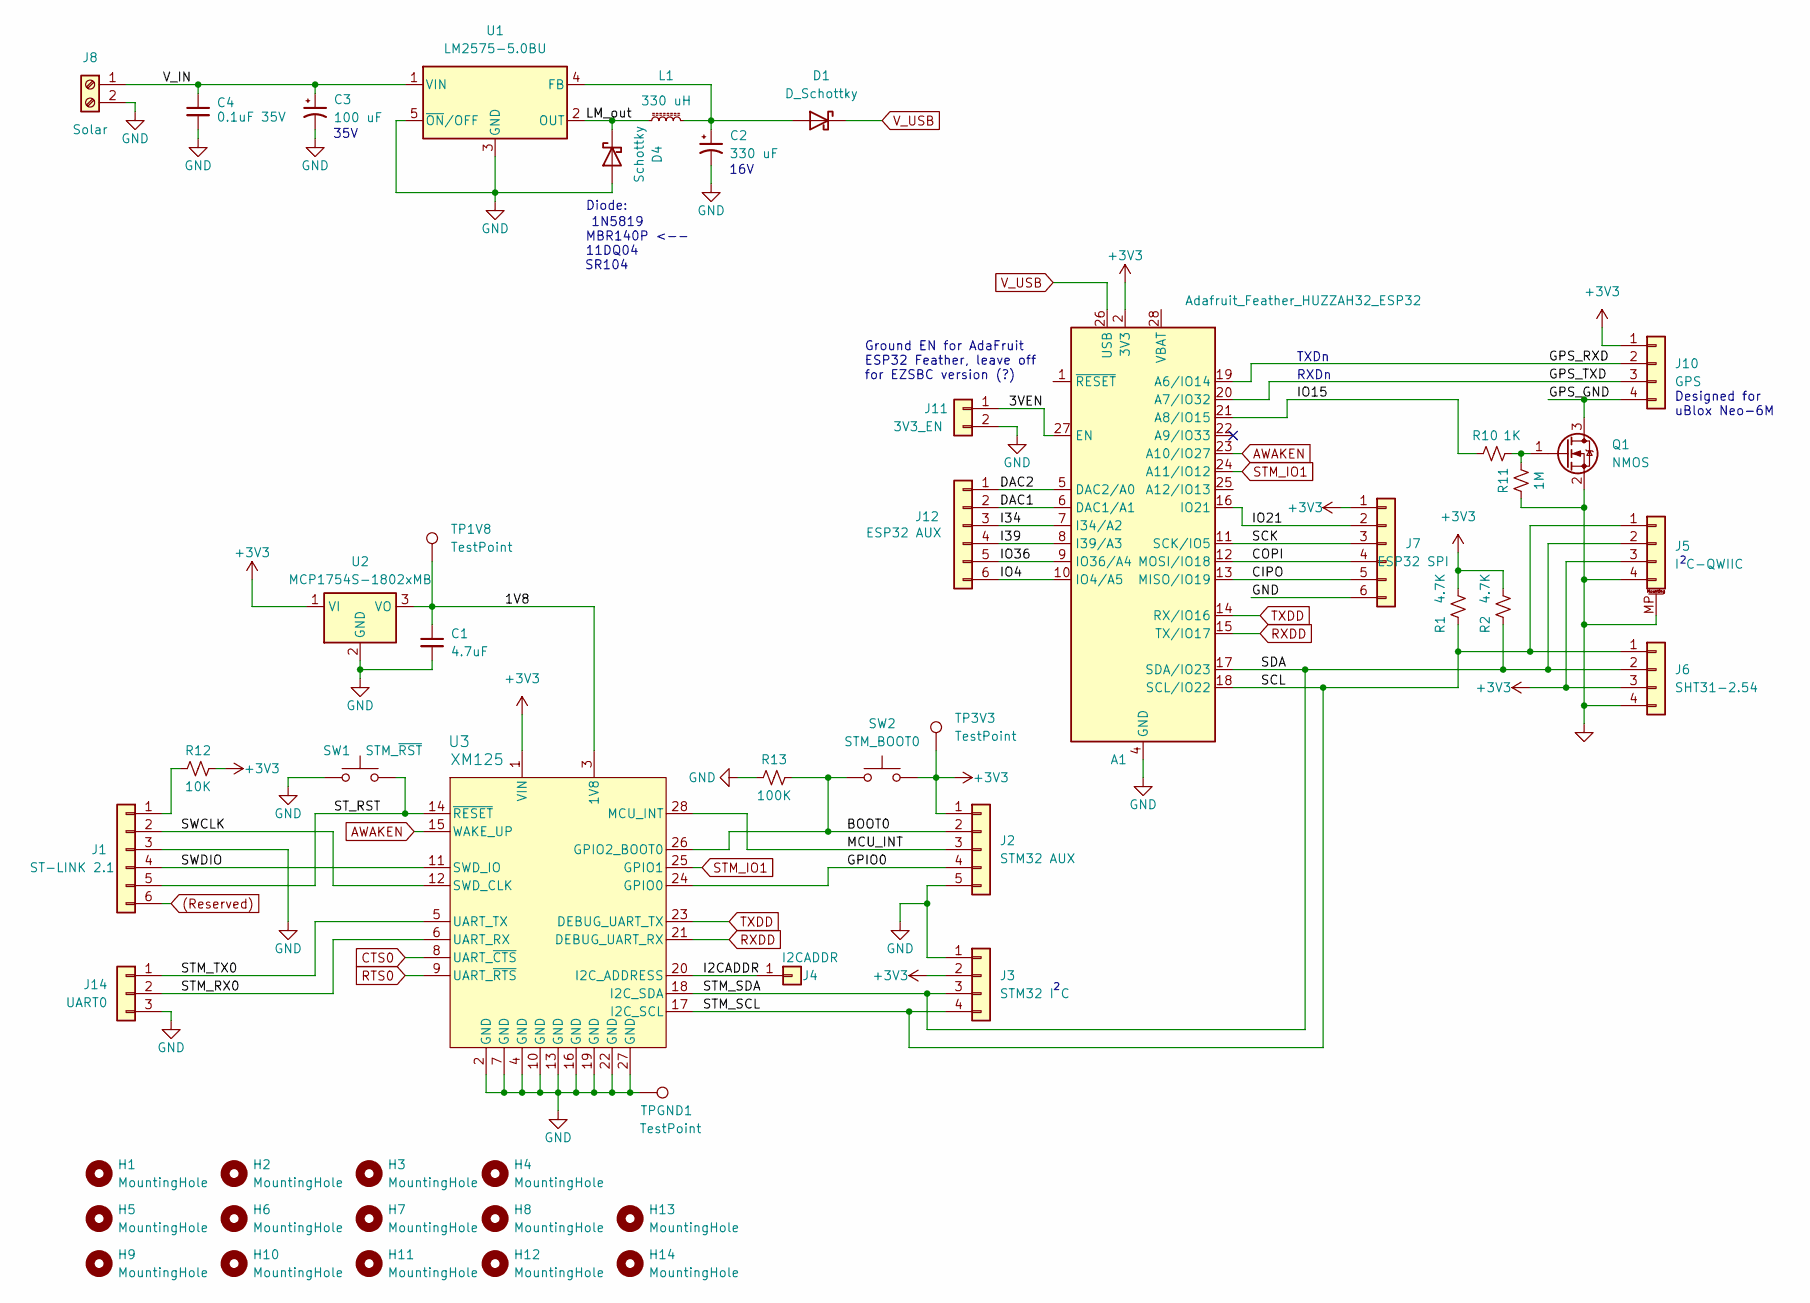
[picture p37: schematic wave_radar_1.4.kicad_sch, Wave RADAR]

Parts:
A1: Adafruit_Feather_HUZZAH32_ESP32; Adafruit_Feather
C1: 4.7uF; C_0805_2012Metric
C2: 330 uF; CP_Radial_D8.0mm_P3.50mm
C3: 100 uF; CP_Radial_D8.0mm_P3.50mm
C4: 0.1uF 35V; C_0805_2012Metric
D1: D_Schottky; D_1206_3216Metric
D4: Schottky; D_1206_3216Metric
H1, H2, H3, H4, H5, H6, H7, H8, H9, H10, H11, H12, H13, H14: MountingHole; MountingHole_2.7mm
J1: ST-LINK 2.1; PinHeader_1x06_P2.54mm_Vertical
J2: STM32 AUX; PinHeader_1x05_P2.54mm_Vertical
J3: STM32 I C; PinHeader_1x04_P2.54mm_Vertical
J4: I2CADDR; PinHeader_1x01_P2.54mm_Vertical
J5: I C-QWIIC; JST_SH_BM04B-SRSS-TB_1x04-1MP_P1.00mm_Vertical
J6: SHT31-2.54; PinHeader_1x04_P2.54mm_Vertical
J7: ESP32 SPI; PinHeader_1x06_P2.54mm_Vertical
J8: Solar; TerminalBlock_Phoenix_MPT-0,5-2-2.54_1x02_P2.54mm_Horizontal
J10: GPS; PinSocket_1x04_P2.54mm_Vertical
J11: 3V3_EN; PinHeader_1x02_P2.54mm_Vertical
J12: ESP32 AUX; PinHeader_1x06_P2.54mm_Vertical
J14: UART0; PinHeader_1x03_P2.54mm_Vertical
L1: 330 uH; Inductors for LM2575, Pulse PE-xxxxx
Q1: NMOS; SOT-23
R1, R2: 4.7K; R_0805_2012Metric
R10: 1K; R_0805_2012Metric
R11: 1M; R_0805_2012Metric
R12: 10K; R_0805_2012Metric
R13: 100K; R_0805_2012Metric
SW1: STM_~{RST}; SW_PUSH_1P1T_6x3.5mm_H4.3_APEM_MJTP1243
SW2: STM_BOOT0; SW_PUSH_1P1T_6x3.5mm_H4.3_APEM_MJTP1243
TP1V8, TP3V3: TestPoint; TestPoint_Loop_D2.50mm_Drill1.0mm
TPGND1: TestPoint; TestPoint_Loop_D2.50mm_Drill1.0mm
U1: LM2575-5.0BU; TO-263-5_TabPin3
U2: MCP1754S-1802xMB; SOT-223-3_TabPin2
U3: XM125; XM125_ACC

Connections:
(Reserved): J1.6
+3V3: A1.2 (3V3), J2.1, J3.2, J5.3, J6.3, J7.1, J10.1, R1.2, R2.2, R12.2, SW2.2, TP3V3.1, U2.1 (VI), U3.1 (VIN)
/1V8: C1.1, TP1V8.1, U2.3 (VO), U3.3 (1V8)
/3VEN: A1.27 (EN), J11.1
/BOOT0: J2.2, R13.2, SW2.1, U3.26 (GPIO2_BOOT0)
/CIPO: A1.13 (MISO/IO19), J7.5
/COPI: A1.12 (MOSI/IO18), J7.4
/DAC1: A1.6 (DAC1/A1), J12.2
/DAC2: A1.5 (DAC2/A0), J12.1
/GPIO0: J2.4, U3.24 (GPIO0)
/GPS_GND: J10.4, Q1.3 (D)
/GPS_RXD: A1.19 (A6/IO14), J10.2
/GPS_TXD: A1.20 (A7/IO32), J10.3
/I2CADDR: J4.1, U3.20 (I2C_ADDRESS)
/I34: A1.7 (I34/A2), J12.3
/I39: A1.8 (I39/A3), J12.4
/IO4: A1.10 (IO4/A5), J12.6
/IO15: A1.21 (A8/IO15), R10.1
/IO21: A1.16 (IO21), J7.2
/IO36: A1.9 (IO36/A4), J12.5
/LM_out: D4.1 (K), L1.1, U1.2 (OUT)
/MCU_INT: J2.3, U3.28 (MCU_INT)
/SCK: A1.11 (SCK/IO5), J7.3
/SCL: A1.18 (SCL/IO22), J3.4, J5.1, J6.1, R1.1, U3.17 (I2C_SCL)
/SDA: A1.17 (SDA/IO23), J3.3, J5.2, J6.2, R2.1, U3.18 (I2C_SDA)
/STM_RX0: J14.2, U3.6 (UART_RX)
/STM_TX0: J14.1, U3.5 (UART_TX)
/ST_RST: J1.5, SW1.1, U3.14 (~RESET)
/SWCLK: J1.2, U3.12 (SWD_CLK)
/SWDIO: J1.4, U3.11 (SWD_IO)
/V_IN: C3.1, C4.1, J8.1, U1.1 (VIN)
AWAKEN: A1.23 (A10/IO27), U3.15 (WAKE_UP)
CTS0: U3.8 (UART_~CTS)
GND: A1.4 (GND), C1.2, C2.2, C3.2, C4.2, D4.2 (A), J1.3, J2.5, J3.1, J5.4, J5.MP (MountPin), J6.4, J7.6, J8.2, J11.2, J14.3, Q1.2 (S), R11.1, R13.1, SW1.2, TPGND1.1, U1.3 (GND), U1.5 (~ON/OFF), U2.2 (GND), U3.2 (GND), U3.4 (GND), U3.7 (GND), U3.10 (GND), U3.13 (GND), U3.16 (GND), U3.19 (GND), U3.22 (GND), U3.27 (GND)
unnamed: C2.1, D1.2 (A), L1.2, U1.4 (FB)
unnamed: J1.1, R12.1
unnamed: Q1.1 (G), R10.2, R11.2
RTS0: U3.9 (UART_~RTS)
RXDD: A1.15 (TX/IO17), U3.21 (DEBUG_UART_RX)
STM_IO1: A1.24 (A11/IO12), U3.25 (GPIO1)
TXDD: A1.14 (RX/IO16), U3.23 (DEBUG_UART_TX)
V_USB: A1.26 (USB), D1.1 (K)

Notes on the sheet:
SR104
1N5819
35V
Ground EN for AdaFruit ESP32 Feather, leave off for EZSBC version (?)
MBR140P <--
11DQ04
RXDn
16V
Diode:
Designed for uBlox Neo-6M
TXDn

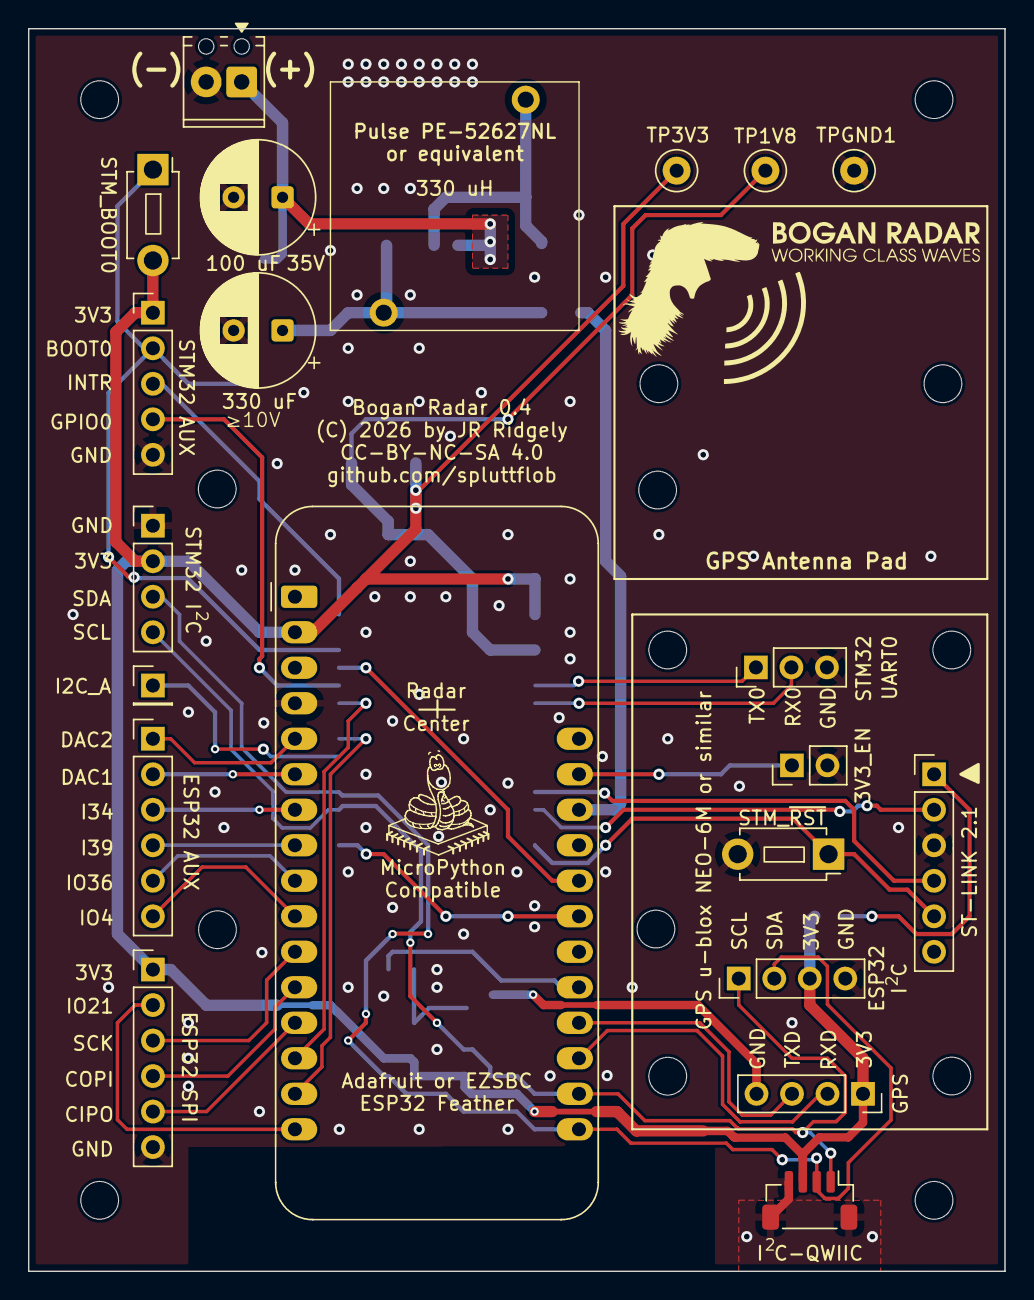
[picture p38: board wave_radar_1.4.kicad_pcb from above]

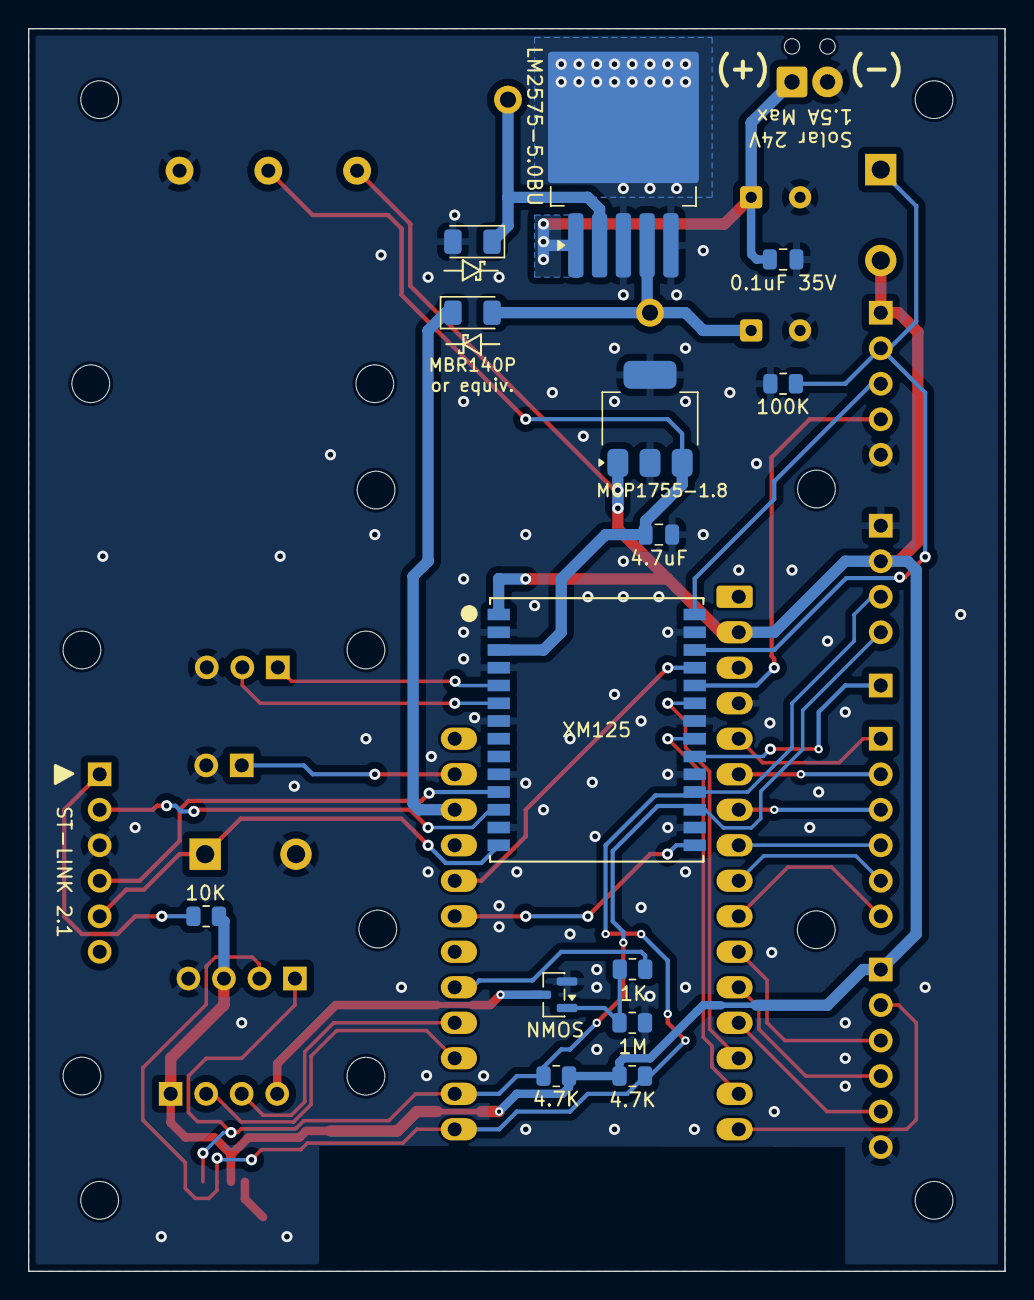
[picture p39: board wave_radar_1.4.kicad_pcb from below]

Board: 2 copper layers, 69.8 x 88.9 mm, 49 parts (14 on the bottom side), 39 nets.

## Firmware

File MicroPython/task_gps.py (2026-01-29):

## @file task_gps.py
#
#  This task sets up and watches a GPS module that keeps track of position and
#  time for a Bogan Radar. It uses a Real-Time Clock (RTC) to hold the time
#  in between GPS fixes.
#
#  The current design uses a PCF8523 RTC on an Adafruit(tm) Adalogger board
#  which can keep time while the ESP32 is powered down. One could also use the
#  RTC inside the ESP32; it would be necessary to wait for the GPS to get a fix
#  before knowing where and when it is if the ESP32's RTC is used, and if the
#  signal isn't too good or the GPS has been off for a while, this can take 
#  many minutes.
#
#  @author Spluttflob
#  @date   2025-Nov-14 Modified heavily from Boatsie GPS
#  @date   2026-Jan-11 Moved stuff from GPS callback to task function
#  @copyright (c) 2025 by Spluttflob, released under the GPL V3

import as_GPS
import machine
import uasyncio as asyncio
import pcf8523


## The local offset from GMT in hours; PDT is -7 and PST is -8
LOCAL_OFFSET = -8

## The pin number of the ESP32 pin connected to the GPS RXD pin
GPS_RXD_PIN_NUM = const(14)

## The pin number of the ESP32 pin connected to the GPS TXD pin
GPS_TXD_PIN_NUM = const(32)

## The pin number of the GPS power pin
GPS_POWER_PIN_NUM = const(15)

## A pin object for the GPS power pin
gps_power_pin = machine.Pin(GPS_POWER_PIN_NUM, machine.Pin.OUT, value=0)

# ## The number of GPS fixes before the real-time clock is updated with GPS time.
# #  A typical GPS might be set up to deliver a fix every 5 seconds; do the math.
# GPS_FIXES_PER_RTC_UPDATE = 720

## An event which triggers the update of the RTCs when the GPS has a good fix.
gps_fix_ready = asyncio.Event()
gps_fix_ready.clear()

## Global reference to the ESP32 RTC, which other tasks will need to use
esp_rtc = machine.RTC()

## A variable which will be set True when a valid date and time from either the
#  PCF8523 RTC or the GPS has been put into the ESP32 RTC
valid_datetime = False

## Callback which runs for each valid GPS fix.
#  @param agps The GPS driver which calls this callback
#  @param *_ A list of other parameters, all of which are ignored
def gps_callback(agps, *_):
    global valid_datetime, gps_fix_ready

    # Update the RTCs with (Y, M, D, h, m, s) once there's a good fix
    # The year must be greater than 2024, else something is amiss
    day, mon, year = agps.date
    if year > 24:
        valid_datetime = True
        gps_fix_ready.set()


## Turn on the GPS module by setting the power control pin high. This
#  assumes that there's an N-channel MOSFET connecting the ground of the
#  GPS module to system ground. If no power pin has been specified, this
#  method does nothing.
def gps_on():
    if gps_power_pin is not None:
        gps_power_pin.value(1)


## Turn off the GPS module by setting the power control pin high. This
#  assumes that there's an N-channel MOSFET connecting the ground of the
#  GPS module to system ground.  If no power pin has been specified, this
#  method does nothing.
def gps_off():
    if gps_power_pin is not None:
        gps_power_pin.value(0)


## The GPS task function which creates the GPS object and processes data
#  strings from it to make information available to other tasks. The task
#  code doesn't do much because the action happens in callbacks in AS_GPS
#  @param i2c The I2C bus which is used to talk to the PCF8523 real-time clock
#  @param data_batch A data batch collector to which GPS data is put for saving
#         to the SD card and sending through MQTT if available
#  @param period_ms How often the GPS is turned on to find time and place
#  @param test_print Whether to print diagnostic data to the serial port
async def gps_task(i2c, data_batch, period_ms=600_000, test_print=False):

    global gps_fix_ready, valid_datetime

    ## The UART (serial port) connected to the GPS module. We use non-standard
    #  pins on the 1.3 board; it's just what has worked out. Because of the
    #  annoying RS-232 naming pin convention, the ESP32's TXD (tx) pin connects
    #  to the GPS's RXD pin and vice versa. For some reason, we need to ensure
    #  that the pin connected to GPS TXD is a regular input, or something
    #  (maybe a pullup?) prevents good GPS signals on the RS-232 line.
    pin_rx = machine.Pin(GPS_TXD_PIN_NUM, machine.Pin.IN)
    uart = machine.UART(2, 9600, bits=8, parity=None, stop=1, flow=0,
                        tx=GPS_RXD_PIN_NUM, rx=GPS_TXD_PIN_NUM)
    pin_rx.init(machine.Pin.IN)

    ## The stream reader which gets data from the UART connected to the GPS
    the_reader = asyncio.StreamReader(uart)

    ## The one and only GPS module that a cheap ocean wave radar needs
    the_gps = as_GPS.AS_GPS(the_reader, local_offset=LOCAL_OFFSET,
                            fix_cb=gps_callback)

    # Create an RTC driver if a PCF8523 seems to be on the I2C bus and copy the
    # time from the PCF8523 to the ESP32 RTC, because the PCF8523 has a battery
    if 0x68 in i2c.scan():
        pcf_rtc = pcf8523.PCF8523(i2c)
        year, mon, day, hrs, mns, scs = pcf_rtc.datetime
        esp_rtc.datetime([year, mon, day, 0, hrs, mns, scs, 0])
        valid_datetime = True
        print(f"Set ESP32 RTC to {esp_rtc.datetime()} from PCF8523")
    else:
        pcf_rtc = None

    while True:
        # Turn on the GPS, then wait until it has a good fix
        gps_on()

        await gps_fix_ready.wait()

        day, mon, year = the_gps.date
        hrs, mns, scs = the_gps.local_time
        year += 2000

        # Update the fancy PCF8523 RTC and the ESP32's built-in RTC
        print(f"Updating RTCs at {year}-{mon}-{day} {hrs}:{mns:02d}:{scs:02d}")
        esp_rtc.datetime([year, mon, day, 0, hrs, mns, scs, 0])
        if pcf_rtc is not None:
            pcf_rtc.datetime = [year, mon, day, hrs, mns, scs]
        valid_datetime = True

        # Put the GPS position into the data batch for sending and/or saving
        lat = the_gps.latitude()
        lon = the_gps.longitude()
        alt = the_gps.altitude
#         node = task_mqtt.ip_node
        fix_it = f"G{lat[1]},{lat[0]},{lon[1]},{lon[0]},{alt}\r\n"
        await data_batch.put(fix_it.encode())
        del fix_it

        # Turn off the GPS; we'll turn it on to get the next fix
        gps_fix_ready.clear()
        gps_off()
        the_reader.close()

        if test_print:
            hrs, mns, scs = the_gps.local_time
            print(f"GPS {hrs}:{mns:02d}:{scs:02d}, ", end='')
            print(f"TsF: {the_gps.time_since_fix():6d}, ", end='')
            print(f"V:{the_gps._valid:08b}, ", end='')
            print(f"{the_gps.latitude()} {the_gps.longitude()}")

        await asyncio.sleep_ms(period_ms)


# ================================ TEST CODE ===================================
if __name__ == "__main__":

    # Used so the GPS can update the PCF8523 real-time clock if it's there
    i2c = machine.I2C(0, scl=machine.Pin(22), sda=machine.Pin(23))
    print(f"I2C devices: " + ",".join(f"0x{item:x}" for item in i2c.scan()))

    # A task which echoes what the GPS sends, just for debugging
    def echo_task():
        print("GPS echo test task")
        gps_on()
        while True:
            if uart.any():
                try:
                    print(uart.read().decode(), end='')
                except UnicodeError:
                    print("*", end='')


    # Choose one of the two task functions, echo to see if the GPS module is
    # sending any data or the real GPS task which can print information from
    # the parser which makes sense of what the GPS module is reporting.
    async def main():
#         asyncio.create_task(echo_task())
        asyncio.create_task(gps_task(i2c, period_ms=10_000, test_print=True))

        await asyncio.sleep_ms(86_400_000)


    print("Beginning GPS parser test.")
    try:
        asyncio.run(main())
    except KeyboardInterrupt:
        print("Ctrl-C. ", end='')

    asyncio.new_event_loop()
    print("Test finished.")

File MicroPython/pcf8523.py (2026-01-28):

## PCF8523 Real Time Clock (RTC) module for MicroPython
#
#  Nov. 2025 Spluttflob made minor changes to MicroPython version, added tests
#  Jun. 2020 Meurisse D. for MCHobby (shop.mchobby.be) ported to MicroPython
#  Nov. 2016 Philip R. Moyer and Radomir Dopieralski for Adafruit Industries
#            - original version for CircuitPython
#
#  - Milliseconds are not supported by this RTC.
#  - Datasheet: http://cache.nxp.com/documents/data_sheet/PCF8523.pdf
#  - based on https://github.com/adafruit/Adafruit_CircuitPython_PCF8523.git
#
# The MIT License (MIT)
#
# Original Arduino program Copyright (c) 2016 Philip R. Moyer and Radomir
# Dopieralski for Adafruit Industries.
#
# Code from https://github.com/mchobby/esp8266-upy/tree/master/pcf8523
#
# BUG: Something in here thinks January 2026 is the 13th month of 2025...!
#
# __version__ = "0.0.1"

import utime as time

STANDARD_BATTERY_SWITCHOVER_AND_DETECTION = 0b000
BATTERY_SWITCHOVER_OFF = 0b111

RTC_REG = 0x03
ALARM_REG = 0x0A
CONTROL_1_REG = 0x00


## Convert binary coded decimal to binary.
def bcd2bin(value):
    return value - 6 * (value >> 4)


## Convert a binary value to binary coded decimal.
def _bin2bcd(value):
    return value + 6 * (value // 10)


## Interface to the PCF8523 Real Time Clock.
class PCF8523:

    ## Initialize the PCF8523 driver object.
    #  @param i2c An I2C bus object which has already been set up
    #  @param address The address of the PCF8523 on the I2C bus
    def __init__(self, i2c, address=0x68):
        self.i2c = i2c
        self.address = address
        self.buf1 = bytearray(1)
        self.buf7 = bytearray(7)

        # Try and verify this is the RTC we expect by checking the timer B
        # frequency control bits which are 1 on reset and shouldn't ever be
        # changed.
        self.retries = 2
        while self.retries > 0:
            self.buf1[0] = 0x12
            self.i2c.writeto(self.address, self.buf1)
            self.i2c.readfrom_into(self.address, self.buf1)
            if (self.buf1[0] & 0b00000111) != 0b00000111 and self.retries == 2:                
                self.soft_reset()
            elif (self.buf1[0] & 0b00000111) != 0b00000111 and self.retries == 1:
                raise ValueError("Unable to find PCF8523 at i2c address 0x68.")
            self.retries -= 1


    ## Send a reset command to the RTC chip.
    def soft_reset(self):
        self.buf1 = bytearray(1)
        self.buf1[0] = 0x58
        # writes 0x58 to address 0x00 to reset the chip
        self.i2c.writeto_mem(self.address, CONTROL_1_REG, self.buf1)


    ## Get the date and time from a given register location (0x03 for RTC,
    #  0x0A for alarm).
    def _read_datetime(self, time_reg):
        weekday_offset = 1
        weekday_start  = 0

        self.buf1[0] = time_reg
        self.i2c.writeto(self.address, self.buf1)
        self.i2c.readfrom_into(self.address, self.buf7)
        # CircuitPython struct_time (tm_year=1999, tm_mon=12, tm_mday=31,
        #   tm_hour=17, tm_min=4, tm_sec=58, tm_wday=4, tm_yday=365, tm_isdst=0)
        # MicroPython mktime (year, month, mday, hour, minute, second, weekday,
        #                     yearday)
        return time.mktime((
                bcd2bin(self.buf7[6]) + 2000,
                bcd2bin(self.buf7[5]),
                bcd2bin(self.buf7[4 - weekday_offset]),
                bcd2bin(self.buf7[2]),
                bcd2bin(self.buf7[1]),
                bcd2bin(self.buf7[0] & 0x7F),
                bcd2bin(self.buf7[3 + weekday_offset] - weekday_start),
                -1,
                -1))


    ## Get a string which holds the date and time from the RTC.
    #  @param time_reg The register to read, actual time or alarm time
    #  @param date Whether to put the date in the string before the time
    #  @param extras Whether to show the day of week and day of year also
    def get_datetime_str(self, time_reg, date=False, extras=False):
        self.buf1[0] = time_reg
        self.i2c.writeto(self.address, self.buf1)
        self.i2c.readfrom_into(self.address, self.buf7)

        str = ""
        if date:
            str += f"{2000 + bcd2bin(self.buf7[6])}-{bcd2bin(self.buf7[5])}-{bcd2bin(self.buf7[3])},"
        str += f"{bcd2bin(self.buf7[2]):02d}:{bcd2bin(self.buf7[1]):02d}:{bcd2bin(self.buf7[0]):02d}"
        if extras:
            str += f",dow:{bcd2bin(self.buf7[4])},"   # dow:{bcd2bin(self.buf7[7])}"
        return str


    ## Set the time from the tuple (year, month, mday, hour, minute, second,
    #  weekday, yearday) on the given register (0x03 for RTC, 0x0A for alarm)
    def _write_datetime(self, time_reg, value):
        weekday_offset = 1
        weekday_start  = 0

        self.buf7[0] = _bin2bcd(value[5]) & 0x7F    # tm_sec format conversions
        self.buf7[1] = _bin2bcd(value[4])           # tm_min
        self.buf7[2] = _bin2bcd(value[3])           # tm_hour
        self.buf7[3 + weekday_offset] = _bin2bcd(
            value[6] + weekday_start                # tm_wday
        )
        self.buf7[4 - weekday_offset] = _bin2bcd(value[2]) # tm_mday
        self.buf7[5] = _bin2bcd(value[1]) # tm_mon
        self.buf7[6] = _bin2bcd(value[0] - 2000) # tm_year

        self.i2c.writeto_mem(self.address, time_reg, self.buf7)


    ## Gets the current date and time. Just gets the important fields:
    #  Year, month, day-of-month, hours, minutes, seconds.
    @property
    def datetime(self):
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

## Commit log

2025-11-08 Rearranged directories and began README
    [QTY1_radar_mount_A.STL, QTY1_radar_mount_B.STL, box_mount.SLDPRT, stick_mount.SLDPRT]
2025-11-08 Added custom PCB designs to hardware/
    [wave_radar_1.3.kicad_pcb, wave_radar_1.3.kicad_sch]
2025-11-09 Added drawing of first try horn antenna, more README updates
    [horn_antenna_1.FCStd]
2025-11-29 Got basic MicroPython firmware running; removed XM125 stuff
    We're using the stock XM125 applications with the MicroPython firmware, so a custom XM125 program isn't needed at this time.
    [antenna_holder.FCStd, antenna_holder.stl, wave_radar_BOM_1.3.xlsx]
2025-12-02 Show board mounting area on hack_bottom_xz.jpg
2025-12-03 Refactorficationized and de-obfuscated README.md (somewhat)
2025-12-12 Minor cleanup, preparing for first deployment
    [horn_antenna_1.FCStd]
2025-12-13 README updates, moved objects
    The SD card, GPS, and UART objects are moved to files for the tasks which use them.
    GPS pins are changed (seemed to be wrong ones?) and a bug fixed where the GPS TXD (ESP32 RXD) pin was configured by MicroPython in a way that prevented reliable GPS data transmission.
    MQTT topic name is configured using the configuration file site name.
    [antenna_holder.FCStd, antenna_holder.stl]
2026-01-28 Update README with note on board version obsolescence
    Added note about the obsolescence of version 1.3 and upcoming boards.
2026-06-02 Added version 1.4 of circuit board; modified README (partly) to explain this
    [wave_radar_1.3_OLD.kicad_pcb, wave_radar_1.3_OLD.kicad_sch, wave_radar_1.4.kicad_pcb, wave_radar_1.4.kicad_sch]

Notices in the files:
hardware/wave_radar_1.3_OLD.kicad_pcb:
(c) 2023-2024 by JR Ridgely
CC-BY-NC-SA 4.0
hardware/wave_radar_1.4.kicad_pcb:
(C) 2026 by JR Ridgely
